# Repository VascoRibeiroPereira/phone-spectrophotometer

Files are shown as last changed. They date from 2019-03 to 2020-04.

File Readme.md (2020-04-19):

# Phone Spectrophotometer

+ [Version française](#spectrophotometre-pour-telephone)

## <U> Overview </U>

This repository includes all elements related with the Phone Spectrophotometer hardware, facilitating its reproduction by anyone.

Many branches of science makes use of spectrophotometers.
The spectrophotometer is an expensive device with the ability to:
<ul>
  <li>Identify an unknown substance</li>
  <li>Quantify a known substance</li>
</ul>

Other common use of spectroscopy with the upmost importance is <b>Teaching</b> the instrumental technique and [Beer'slaw](https://en.wikipedia.org/wiki/Beer%E2%80%93Lambert_law).

The Phone Spectrophotometer is an open source hardware that comits with a reduced cost of production, open source and available for everyone, and uses pre-existing technology - your own mobile phone.

You can also find the .stl files for printing at Thingiverse https://www.thingiverse.com/thing:3185420

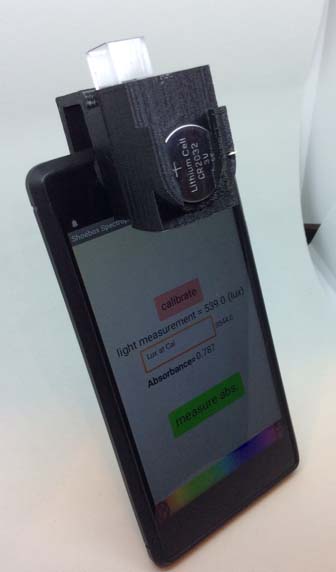
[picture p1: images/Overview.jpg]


This work is licensed under a Solderpad Hardware Licence Version 2.0

## Spectrophotometre pour telephone

### <U>Vue d'ensemble</U>

Ce dépôt comprend tous les éléments liés au matériel du spectrophotomètre pour un ordiphone, facilitant sa reproduction par quiconque.

De nombreuses branches de la science utilisent des spectrophotomètres. Le spectrophotomètre est un appareil coûteux qui permet de :

<ul>
    <li>D'identifier une substance inconnue</li>
    <li>Quantifier une substance connue</li>
</ul>

<b>L'enseignement</b> de la technique des instruments et de la [loi de Beer](https://fr.wikipedia.org/wiki/Loi_de_Beer-Lambert) est un autre usage courant de la spectroscopie qui revêt une importance capitale.

Le spectrophotomètre pour ordiphone est un matériel à code source ouvert, à coût de production réduit, disponible pour toute personne, et qui utilise une technologie préexistante - votre propre téléphone portable.

Vous pouvez également trouver les fichiers .stl à imprimer sur le site Thingiverse <https://www.thingiverse.com/thing:3185420>



Cette réalisation est sous licence Solderpad Hardware Licence Version 2.0

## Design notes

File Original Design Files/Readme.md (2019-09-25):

# Original and Auxiliary Design Files

You will find here the original design files, all made with <i> SketchUp Make</i>, in .skp (its native proprietary format).

To edit it you'll need to download SketchUp Make from [here](https://www.sketchup.com/download/make)

If you only want the auxiliary design files you can use the stereolithography file format (.stl)

___
## Add of the steadyversion!

The Steady Version solves an issue related to the block position not being fixed into the Phone holder. This way it allows more confidence in calibration curves and further results with reproducibility.

_Important note_: I recommend printing the LED Block - Steady Version horizontally.

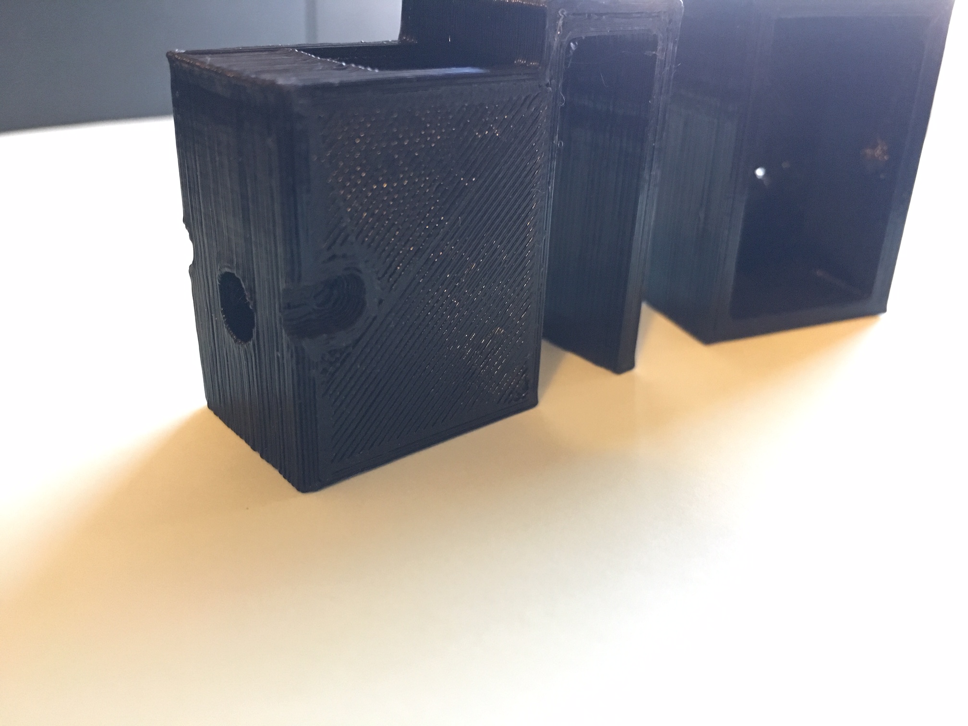
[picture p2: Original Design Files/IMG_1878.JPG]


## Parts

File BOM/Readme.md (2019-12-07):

<h1> Bill of Materials</h1>

|Designator|Description                |Suplier                      |Part Number    |Price |Link                                                                                                                                                                                                           |Notes                                         |
|----------|---------------------------|-----------------------------|---------------|---------|---------------------------------------------------------------------------------------------------------------------------------------------------------------------------------------------------------------|----------------------------------------------|
|A         |LED 400nm                  |SparkFun                     |COM-08662      |0.84 €|https://www.sparkfun.com/products/8662                                                                                                                                                                         |                                              |
|B         |LED 465nm                  |SparkFun                     |COM-00529      |0.30 €|https://www.sparkfun.com/products/9662                                                                                                                                                                         |Quantity discount                             |
|C         |LED 587nm                  |SparkFun                     |COM-00530      |0.30 €|https://www.sparkfun.com/products/10023                                                                                                                                                                        |Quantity discount                             |
|D         |PLA LED Block              |Self Made                    |N/A            |0.22 €|https://fillamentum.com/products/fillamentum-pla-extrafill-traffic-black                                                                                                                                       |Price calculated for the material used (8g)   |
|E         |CR2032 Battery             |SparkFun                     |PRT-00338      |1.71 €|https://www.sparkfun.com/products/338                                                                                                                                                                          |                                              |
|F         |PLA Cuvette Holder         |Self Made                    |N/A            |0.34 €|https://fillamentum.com/products/fillamentum-pla-extrafill-traffic-black                                                                                                                                       |Price calculated for the material used (12g)  |
|G         |Plastic Cuvette            |BrandTech                    |759071D        |0.17 €|https://www.brandtech.com/product/ps-and-pmma-cuvettes/                                                                                                                                                        |Sold in pack of 100. Price for single cuvette.|
|H         |Self-adhesive Holled Rubber|Yelanon                      |ASIN B07NSV2L6B|0.33 €|https://www.amazon.com/Yelanon-Furniture-Pads-Slip-Rubber/dp/B07NSV2L6B/ref=sr_1_30_sspa?crid=220LWP6C13XBT&keywords=furniture+pads&qid=1551634657&s=gateway&sprefix=furniture+%2Caps%2C255&sr=8-30-spons&psc=1|Quantity discount                             |
|I         |Mobile phone               |N/A                          |N/A            |N/A   |N/A                                                                                                                                                                                                            |Pre-existing technology                       |
|J         |Software                   |Shoebox spectrophotometer APP|N/A            |Free  |https://play.google.com/store/apps/details?id=appinventor.ai_billhosker.Shoeboxspec&hl=pt_PT                                                                                                                   |                                              |

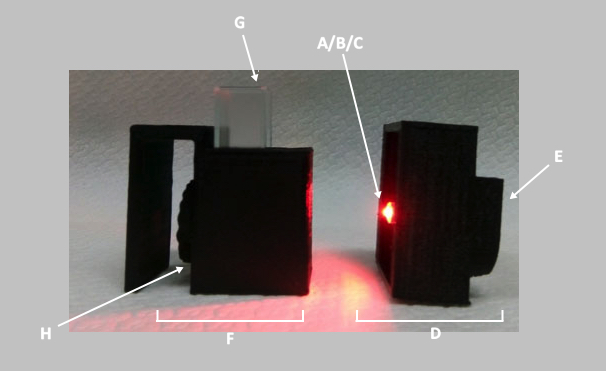
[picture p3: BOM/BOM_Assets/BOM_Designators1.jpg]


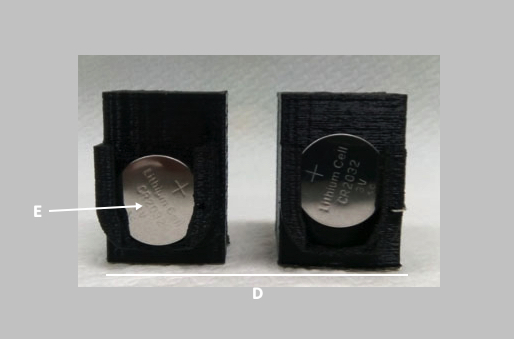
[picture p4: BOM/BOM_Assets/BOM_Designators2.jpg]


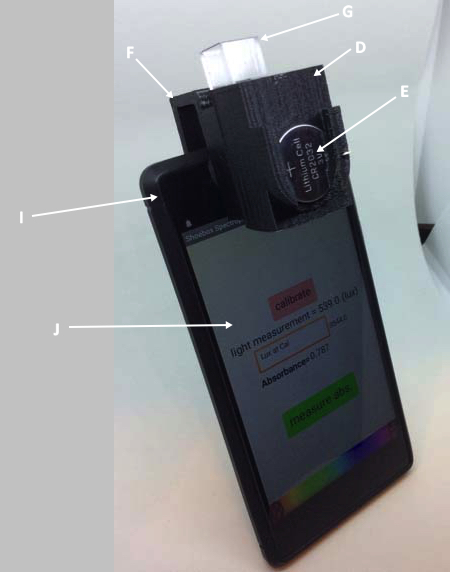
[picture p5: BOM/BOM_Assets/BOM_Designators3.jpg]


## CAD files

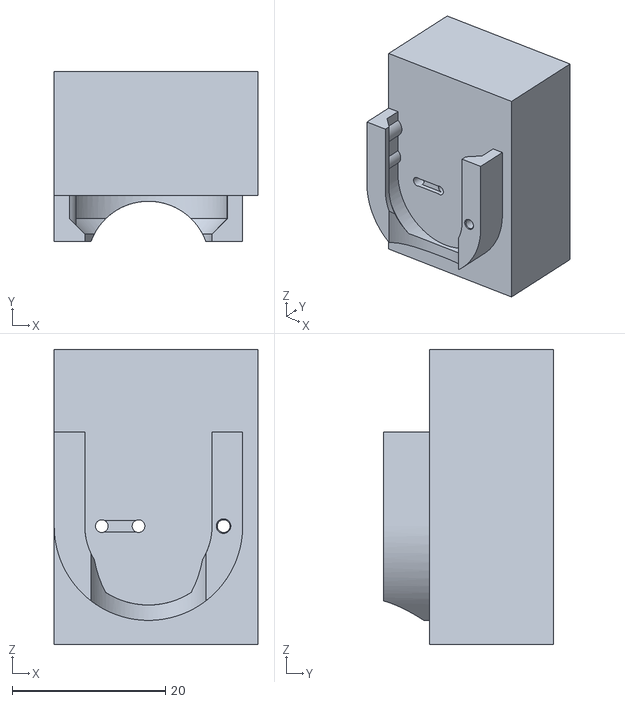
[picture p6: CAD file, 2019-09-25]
Original Design Files/SteadyLEDBlock.stl
26.6 x 22.2 x 38.5

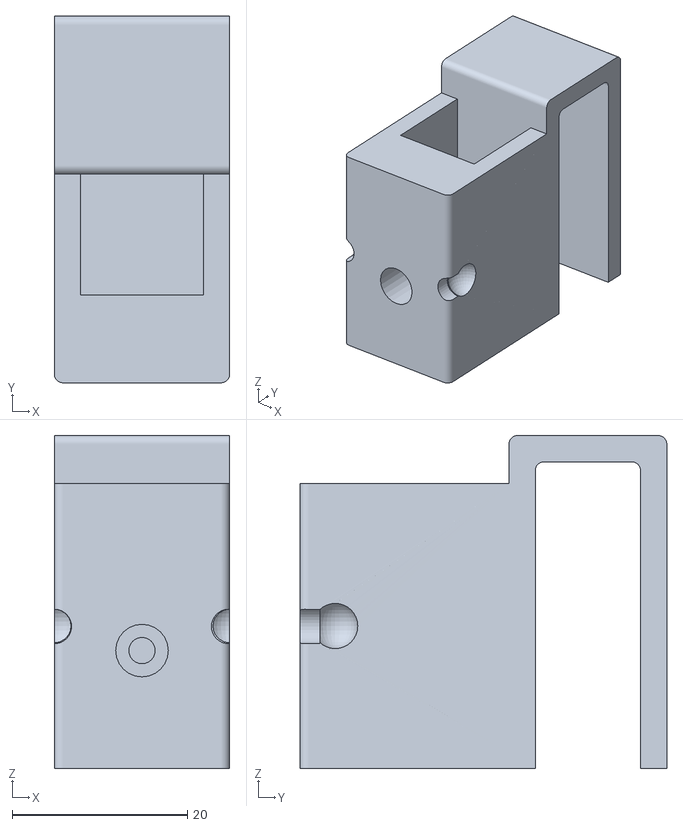
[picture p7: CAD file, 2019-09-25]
Original Design Files/SteadyPhoneHolder.stl.stl
20.0 x 41.8 x 38.0

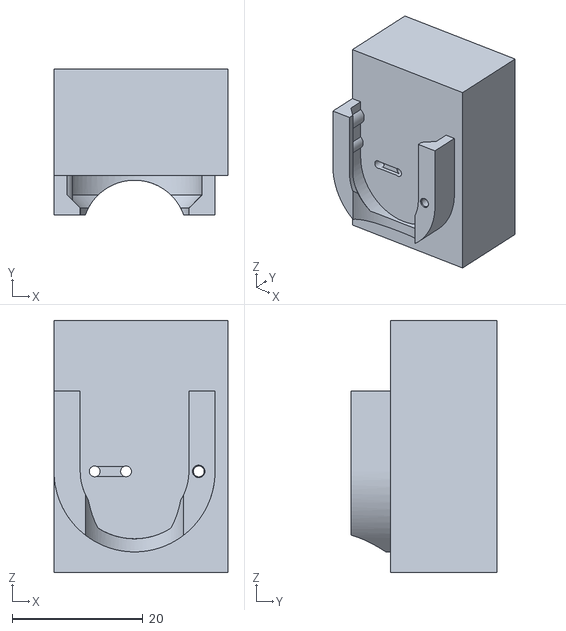
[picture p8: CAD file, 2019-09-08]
Original Design Files/LED_Block.stl
26.6 x 22.2 x 38.5

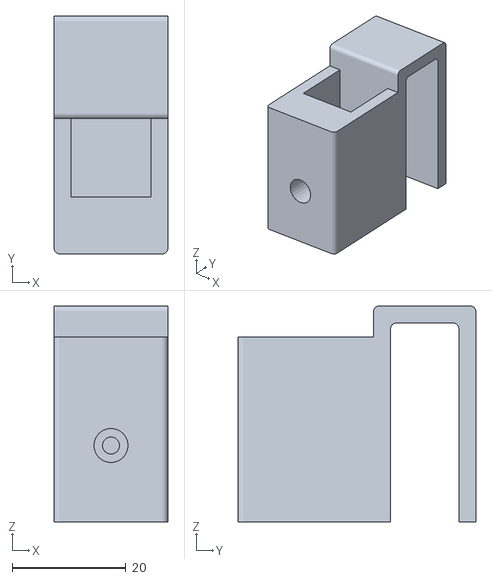
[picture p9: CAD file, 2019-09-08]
Original Design Files/Spectrometer.stl
20.0 x 41.8 x 38.0

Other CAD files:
Original Design Files/Phone Spectrophotometer.skp
Original Design Files/SteadyVersion.skp

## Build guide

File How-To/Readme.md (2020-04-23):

+ [Version française](#comment-travailler-avec-le-spectrophotometre-sur-ordiphone)

## How to Work With the Phone Spectrophotometer

The Phone Spectrophotometer is quite easy to work with. You'll find here documentation showing how to work with it, some advices/troubleshootings and also suggestions of activities.

After the assembly of the <b>LED Block</b> and <b>Cuvette Holder</b> is time to test it out.

To do so, you’ll need an Android Phone with the Shoebox Spectrophotometer APP installed (here on play store https://play.google.com/store/apps/details?id=appinventor.ai_billhosker.Shoeboxspec&hl=en_US and here the source Apk https://androidcrew.com/app/appinventor.ai_billhosker.Shoeboxspec). You can also try other APPs with Ambient Light Sensor measurement.

<i>Note: In iPhone and iPad you can also use alternative APPs but they will measure the light on camera and not on the Light Sensor (usually next to the front camera of your phone).</i>

Turn on the LED by putting the coin battery CR2032 in the on-position (figure 1).



<i>Figure 1. Coin battery in on-position (left) and off-position (right)</i>

Next install the model in the phone with the APP launched and try to get an high value of light measurement (figure 2).

<i>Note: Some phone sensors may be more sensible to light than others, causing them to saturate (give a maximum value). The value obtained from a saturated sensor can not be used because it means the sensor can’t read all the light thats reaching it. Try to misalign the model just enough for the value of the light measurement seams to variate.</i>



<i>Figure 2. Assembled model and phone with the Shoebox Spectrophotometer launched</i>

Now is up to what you want to test! Try the examples in the <b>booklet of spectroscopy activities</b> for you to get used with the technic and the hardware/software.

<ins>Note: If you use other softwares you’ll need to calculate manually the absorbance based on the Raw Data obtained (light measurement).</ins>

You can make the <b>LED Block</b> with many different LED colours. Here are some typical emission wavelengths from coloured LEDs.

<b>Typical LED Wavelengths</b>

Red Light Diodes - 625nm

Green Light Diodes - 525nm

Blue Light Diodes - 465nm

Orange Light Diodes - 610nm

Yellow Light Diodes - 575nm

<em>Special LEDs</em>

IR Light Diodes - 950nm

UV Light Diodes - 400nm

## Comment travailler avec le spectrophotometre sur ordiphone

Le spectrophotomètre avec odiphone est assez facile à utiliser. Vous trouverez ici une documentation montrant comment l'utiliser, quelques conseils et dépannages ainsi que des suggestions d'activités.

Après l'assemblage du <b>bloc LED</b> et du porte-cuvette, il est temps de le tester.

Pour ce faire, vous aurez besoin d'un téléphone Android avec l'application spectrophotomètrie Shoebox installée (ici sour le play store https://play.google.com/store/apps/details?id=appinventor.ai_billhosker.Shoeboxspec&hl=en_US et ici son Apk https://androidcrew.com/app/appinventor.ai_billhosker.Shoeboxspec). Vous pouvez également essayer d'autres APP avec la mesure du capteur de lumière ambiante.

<i>Remarque : sur l'iPhone et l'iPad, vous pouvez également utiliser d'autres APP mais elles mesureront la lumière sur l'appareil photo et non sur le capteur de lumière (généralement à côté de l'appareil photo avant de votre téléphone).</i>

Allumez la LED en mettant la pile CR2032 en position allumée (figure 1).



<i>Figure 1. Batterie de pièces en position marche (à gauche) et en position arrêt (à droite)</i>

Ensuite, installez le modèle dans le téléphone avec l'application lancée et essayez d'obtenir une valeur élevée de mesure de la lumière (figure 2).

<i>Remarque : certains capteurs du téléphone peuvent être plus sensibles à la lumière que d'autres, ce qui les fait saturer (donnez une valeur maximale). La valeur obtenue à partir d'un capteur saturé ne peut pas être utilisée car cela signifie que le capteur ne peut pas lire toute la lumière qui l'atteint. Essayez de désaligner le modèle juste assez pour que la valeur de la mesure de la lumière varie.<i>



<i>Figure 2. Modèle assemblé et téléphone avec le spectrophotomètre Shoebox lancé</i>

Maintenant, c'est à vous de choisir ce que vous voulez tester ! Essayez les exemples du <b>livret d'activités sur la spectroscopie</b> pour vous familiariser avec la technique et le matériel/logiciel.

<ins>Note : Si vous utilisez d'autres logiciels, vous devrez calculer manuellement l'absorbance sur la base des données brutes obtenues (mesure de la lumière).</ins>

Vous pouvez fabriquer le <b>bloc de LED</b> avec de nombreuses couleurs de LED différentes. Voici quelques longueurs d'onde d'émission typiques des LED de couleur.

<b>Longueurs d'onde types des LED</b>

Diodes rouges - 625nm

Diodes lumineuses vertes - 525nm

Diodes lumineuses bleues - 465nm

Diodes lumineuses orange - 610nm

Diodes lumineuses jaunes - 575nm

<em>LEDs spéciaux</em>

Diodes lumineuses IR - 950nm

Diodes de lumière UV - 400nm

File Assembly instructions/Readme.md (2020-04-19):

**Assembly instructions**

+ [Version Française](#instruction-pour-assemblage)

After sourcing the materials described in the BOM start assembling the parts as described in this document.

**3D printed parts**

There are two parts to be 3D printed - the PLA LED block and the Cuvette Holder.

You can use a 3D printer service online or in your local community, or even print it yourself.
If you are going to print it yourself the the recommended settings to 3D print are described in the table 1 (using Ultimaker Cura software).

<i>Table 1 - Main characteristics used to 3D print the Phone Spectrometer</i>

|  Characteristic |  Selection |
|:-:|:-:|
| Layer height  |  0.2mm |
|  Wall thickness |  2mm |
| Top/Bottom thickness  | 0.8mm  |
|  Infill density |  20% |
| Printing temperature  | 210ºC  |
|  Retraction | Enabled  |
| Print speed  | 50mm/s  |
| Generate support  |  No |
|  Build plate adhesion type | Brim  |

Since the 3D printed method is by Fused Deposition Manufacturing the layers are horizontal. This means that the cuvette holder may be fragile at some key parts, and may easily snap. We recommend you to 3D print the cuvette holder horizontally so you have a stronger and much durable part to work with (figure 1).

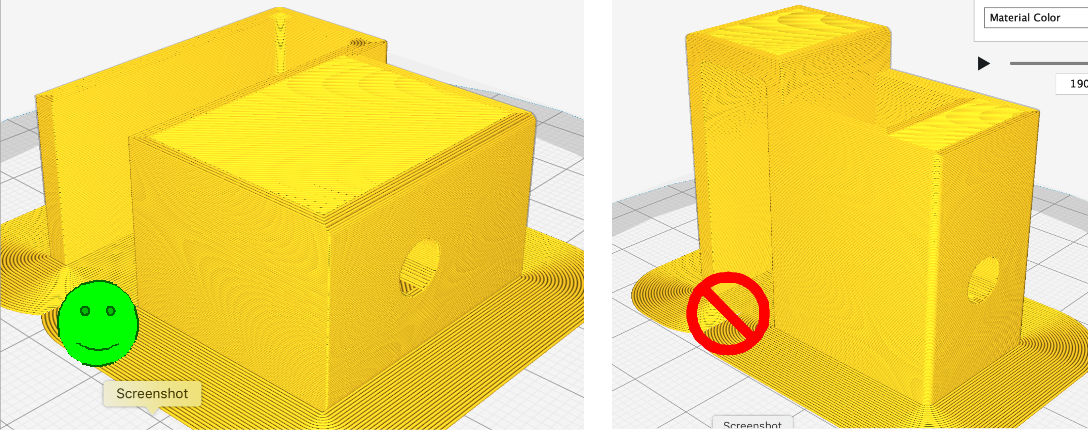
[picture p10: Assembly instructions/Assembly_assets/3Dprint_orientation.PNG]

<i>Figure 1 - Recommended orientation to 3D print the Cuvette Holder</i>

The recommended material to 3D print is a Traffic Black PLA filament (RAL 9017), from Fillamentum Manufacturing Czech s.r.o. or equivalent. 

**Cuvette Holder**

This part only requires the addition of the rubber part (i.e. figure 2)

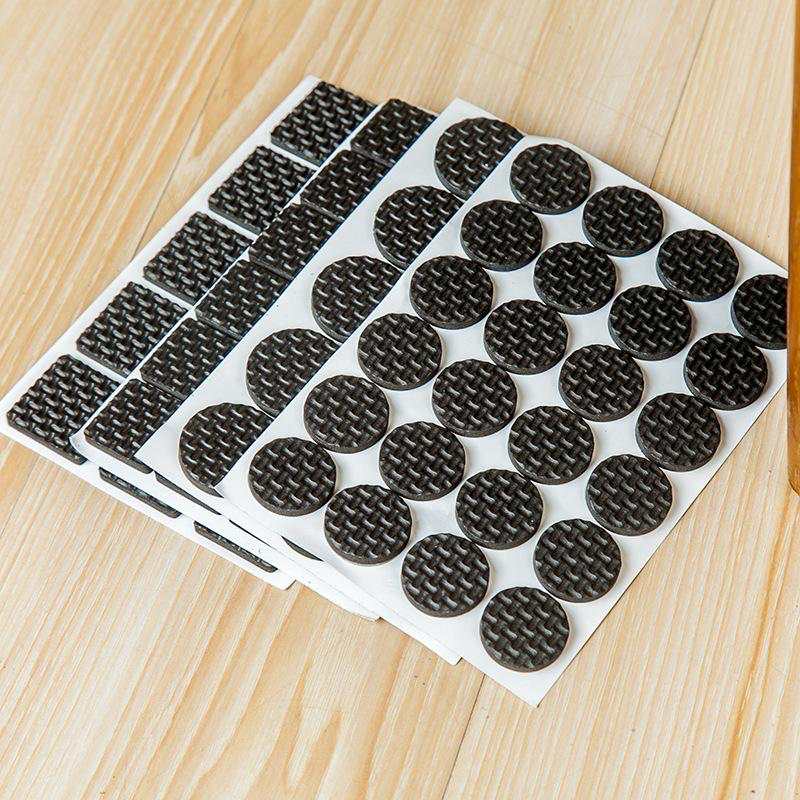
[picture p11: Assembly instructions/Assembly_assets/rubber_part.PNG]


<i>Figure 2 - Rubber part to be glued to the cuvette holder.</i>

Use a puncher to do a hole in the middle of the rubber
Glue it tightly aligned to the rear aperture of the cuvette holder so it will stay between the light exit and the phone sensor - as seen in the BOM designators doc.

This rubber will help you align the rear hole with the phone sensor to get the maximum light measurement possible and also limit the ambient light to interfere with the sensor.

**LED Block**

The LED you choose to use depends on the analyte; for instance, you can have several PLA LED Blocks with different LED mounted and so different emission wavelengths.

To mount the LED you have to identify the LED cathode (-) and anode (+) - figure 3.

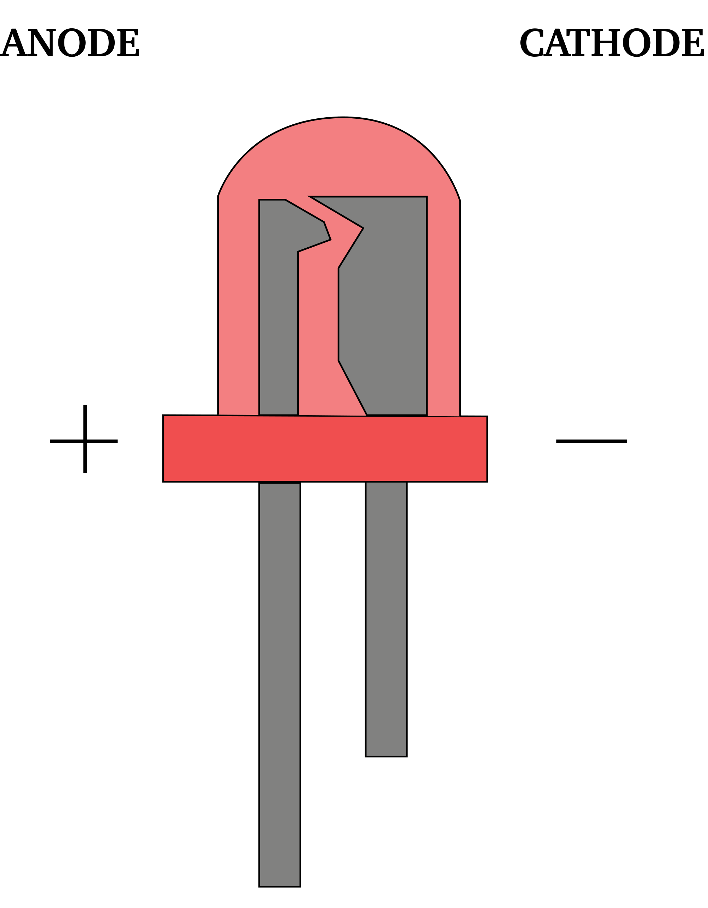
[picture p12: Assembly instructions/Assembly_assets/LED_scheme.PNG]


<i>Figure 3 - A simple scheme of how to identify the cathode and the anode legs of an LED.</i>

Next, mount the LED as specified in figure 4.

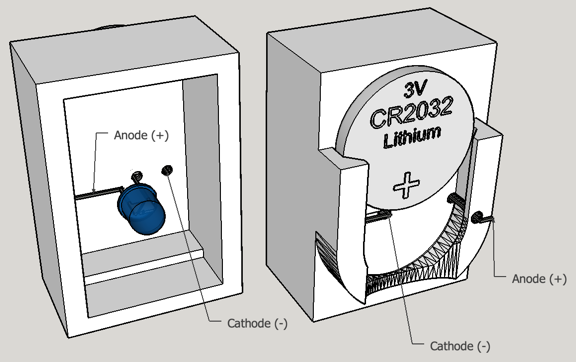
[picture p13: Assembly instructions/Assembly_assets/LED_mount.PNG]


<i>Figure 4 - LED mounted in the printed block, with a CR2032 battery. The anode passes trough the right hole to the outside, touching the battery when it is in the down position and the cathode passes in the first hole to the outside and them to the further left hole to the inside of the model, creating a loop.</i>

The two parts - LED Block and Cuvette Holder fit together and the LED goes inside the front aperture of the Cuvette Holder - it may be necessary to adjust the LED position the first time.

**Finish**

After the assembly of the parts, turn on the LED and mount it with the rear hole pointed near the front camera of your phone. Open the Shoebox Spectrophotometer APP (here on play store https://play.google.com/store/apps/details?id=appinventor.ai_billhosker.Shoeboxspec&hl=en_US and here the source Apk https://androidcrew.com/app/appinventor.ai_billhosker.Shoeboxspec), start moving the model checking the light measure to figure when the light gets to the sensor - you should get reading from 0, when the rear hole is completely misaligned, to a big value like 4000 for example (this depends on the sensor of your phone).

<ins>Note:</ins>

If the LED Block have a loose fit to the Cuvette Holder you may use something so it remains stable (such as a little piece of paper between the models, or an elastic rubber). You may even glue it if you don’t intend to change the LED Block.
The LED Block turns on when the coin battery in down and off when the battery is up.
You can use the LED Block turned on to help you glue the rubber part to the Cuvette Holder.
Do not use the APP when the light measurement seams to be at the highest value possible. Move a little the holder so it slightly misalign with the sensor and gets a more variable value so the sensor is not saturated with light.

## Instruction pour assemblage

Après avoir sélectionné les matériaux décrits dans la nomenclature, commencez à assembler les pièces comme décrit dans ce document.

**Pièces imprimées en 3D**

Il y a deux parties à imprimer en 3D : le bloc LED PLA et le porte-cuvette.

Vous pouvez utiliser un service d'impression 3D en ligne ou dans votre communauté locale, ou même l'imprimer vous-même. Si vous comptez l'imprimer vous-même, les paramètres recommandés pour l'impression 3D sont décrits dans le tableau 1 (à l'aide du logiciel Ultimaker Cura).

<i>Tableau 1 - Principales caractéristiques utilisées pour l'impression 3D du spectromètre téléphonique</i>

| Caractéristiques | Selection |
|:-:|:-:|
| Hauteur de la couche | 0,2 mm |
| Epaisseur de la paroi | 2mm |
| Épaisseur du dessus/du dessous | 0,8 mm |
| Densité de remplissage | 20 |
| Température d'impression | 210ºC |
| Rétraction | activée |
| Vitesse d'impression | 50mm/s |
| Générer un support | Non |
| Construire une plaque d'adhérence typée | Brim |

Comme la méthode d'impression en 3D est celle de la fabrication par dépôt fondu, les couches sont horizontales. Cela signifie que le porte-cuvette peut être fragile à certains endroits clés et peut facilement se casser. Nous vous recommandons d'imprimer en 3D le porte-cuvette à l'horizontale afin d'avoir une pièce plus solide et plus durable pour travailler (figure 1).



<i>Figure 1 - Orientation recommandée pour l'impression 3D du porte-cuvette</i>

Le matériau recommandé pour l'impression 3D est un filament PLA Traffic Black (RAL 9017), de Fillamentum Manufacturing Czech s.r.o. ou équivalent.

**Porte-cuvette**

Cette partie ne nécessite que l'ajout de la partie en caoutchouc (c'est-à-dire la figure 2)



<i>Figure 2 - Pièce en caoutchouc à coller sur le porte-cuvette.</i>

Utilisez un poinçon pour faire un trou au milieu du caout. Cochouc. Collez la pièce fermement alignée sur l'ouverture arrière du porte-cuvette afin qu'elle reste entre la sortie de la lumière et le capteur du téléphone − comme indiqué dans le document des désignations de la nomenclature.

Ce caoutchouc vous aidera à aligner le trou arrière avec le capteur du téléphone pour obtenir la mesure de lumière maximale possible et aussi limiter la lumière ambiante pour interférer avec le capteur.

**Bloc de LED**

La LED que vous choisissez d'utiliser dépend de l'analyte ; par exemple, vous pouvez avoir plusieurs blocs de LED PLA avec différentes LED montées et donc différentes longueurs d'onde d'émission.

Pour monter la LED, vous devez identifier la cathode (-) et l'anode (+) de la LED - figure 3.



<i>Figure 3 - Un schéma simple pour identifier la cathode et les pattes d'anode d'une LED.</i>

Ensuite, montez la LED comme indiqué sur la figure 4.


<i>Figure 4 - LED montée dans le bloc imprimé, avec une pile CR2032. L'anode passe à travers le trou de droite vers l'extérieur, touchant la pile lorsqu'elle est en position basse et la cathode passe dans le premier trou vers l'extérieur et eux dans le trou plus à gauche vers l'intérieur du modèle, créant ainsi une boucle.</i>

Les deux parties - le bloc de LED et le porte-cuvette s'emboîtent et la LED passe dans l'ouverture avant du porte-cuvette - il peut être nécessaire d'ajuster la position de la LED la première fois.

**Terminer**

Après l'assemblage des pièces, allumez la LED et placez la avec sur trou arrière pointé près de la caméra avant de votre téléphone. Ouvrez l 'application de spectrophotomètrie de Shoebox (ici sour le play store https://play.google.com/store/apps/details?id=appinventor.ai_billhosker.Shoeboxspec&hl=en_US et ici son Apk https://androidcrew.com/app/appinventor.ai_billhosker.Shoeboxspec), commencez à déplacer le modèle en vérifiant la mesure de la lumière pour savoir quand la lumière arrive au capteur − vous devriez obtenir une lecture de 0, lorsque le trou arrière est complètement désaligné, à une grande valeur comme 4000 par exemple (cela dépend du capteur de votre téléphone).

<ins>Note :</ins>

Si le bloc de LED est mal ajusté au porte-cuvette, vous pouvez utiliser quelque chose pour qu'il reste stable (comme un petit morceau de papier entre les pièces assemblées, ou un élastique). Vous pouvez même le coller si vous n'avez pas l'intention de changer le bloc de LED. Le bloc LED s'allume lorsque la pile est déchargée et s'éteint lorsque la pile est pleine. Vous pouvez utiliser le Bloc LED allumé pour vous aider à coller la partie en caoutchouc sur le Porte-cuvette. N'utilisez pas l'application lorsque la mesure de la lumière semble être à la valeur la plus élevée possible. Déplacez un peu le support pour qu'il s'aligne légèrement sur le capteur et obtienne une valeur plus variable afin que le capteur ne soit pas saturé de lumière.

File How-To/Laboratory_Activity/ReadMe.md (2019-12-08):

# Laboratory Activity

<ins>Objectives</ins>

**- Lambert-Beer Law verification**

**- Sample Assay**

## Lambert-Beer Law verification

For the experimental activity we will need access to a spectrophotometer and to one or more sets of coloured filters. One can use professional materials or, in this case:

- An Android phone with an ALS (ambient light sensor) and the APP “Shoebox Spectrophotometer"

- Spectrophotometer and light source (fixed wavelength from a LED) made by 3D printing or other creative method.

- Coloured filters with 9mm x 30mm.

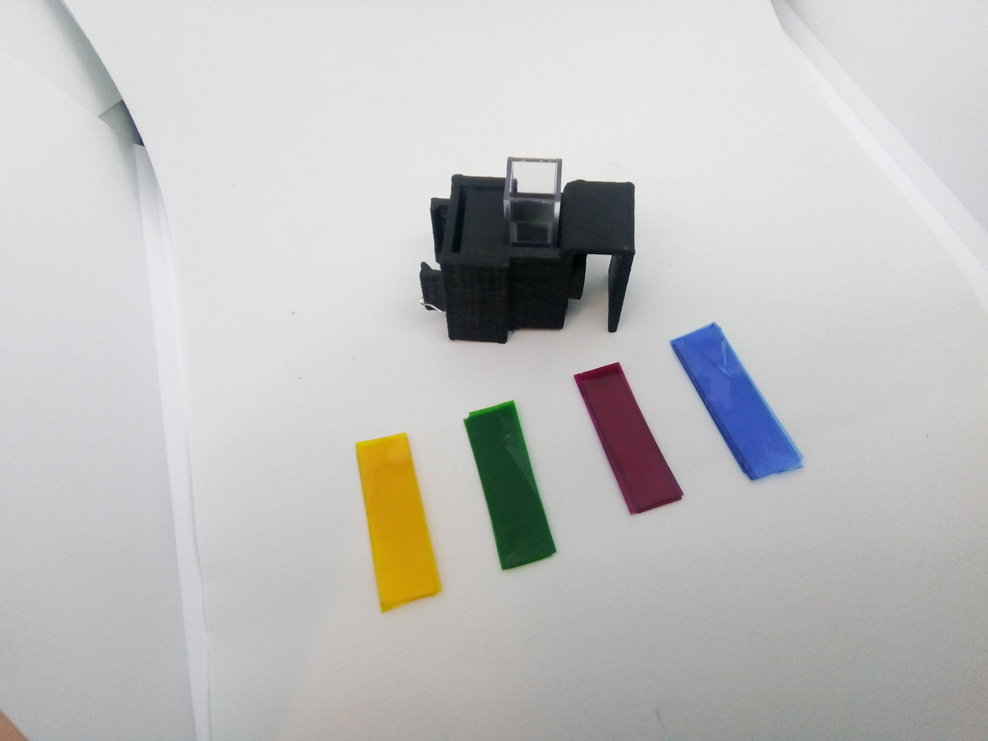
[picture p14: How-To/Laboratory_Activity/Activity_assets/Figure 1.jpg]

*Figure 1 - Fixed wavelength spectrophotometer and filters used*

When using LEDs we assume the wavelengths in the table 1.

*Table 1 - Maximum emitted wavelength of coloured LED*

|LED   |Emitted Wavelengh (max)|
|------|-----------------------|
|Red   |625nm                  |
|Green |525nm                  |
|Blue  |465nm                  |
|Orange|610nm                  |
|Yellow|575nm                  |

### Procedure

1. Mount the spectrophotometer with the LED turned on and with the APP launched.

2. Adjust the equipment until you obtain a LUX reading that is high.

3. Register the approximate value of the LUX measured and take note of this value as you add filters to the spectrometer.

### Data Processing

Assuming that the first value of LUX corresponds to 100% of transmittance, start to calculate the percentage of transmittance of each filter assuming the  previous LUX measure.

#### Questions to be answered:

> All the filters give us the same percentage?
> 
> What can we say about the linearity needed for the Lambert-Beer Law?
_____

**Lets start with this example:**

We used a LED of 525nm (green) and started adding yellow filters. The LUX data are in the table 2.

*Table 2 - Data obtained at 525nm for yellow filters*

|Number of Filters|Lux  |
|-----------------|-----|
|0                |13150|
|1                |9830 |
|2                |7580 |
|3                |5640 |
|4                |4540 |
|5                |3630 |
|6                |2850 |

Next we processed the data in order to understand if we maintain the linearity - if one filter gives us an aberrant reading - out of the expected percentage.

We can check in table 3, that for each new filter added our source loses about 20-25% of intensity. We can say that we must have linearity since the values are in the same order of magnitude.

*Table 3 - % of transmitance for each added filter*

|Number of Filters|% Transmitance|
|-----------------|--------------|
|0                |100           |
|1                |75            |
|2                |77            |
|3                |74            |
|4                |80            |
|5                |80            |
|6                |79            |

After the analysis we can observe the transmittance as we add each filter. The table 4 presents the data expressed in the graphs 1 and 2.

*Table 4 - % of transmitance and absorbance with increased number of added filter*

|Number of Filters|% Transmittance|Absorbance|
|-----------------|---------------|----------|
|0                |100            |0         |
|1                |75             |0,13      |
|2                |58             |0,24      |
|3                |43             |0,37      |
|4                |35             |0,46      |
|5                |28             |0,56      |
|6                |22             |0,66      |

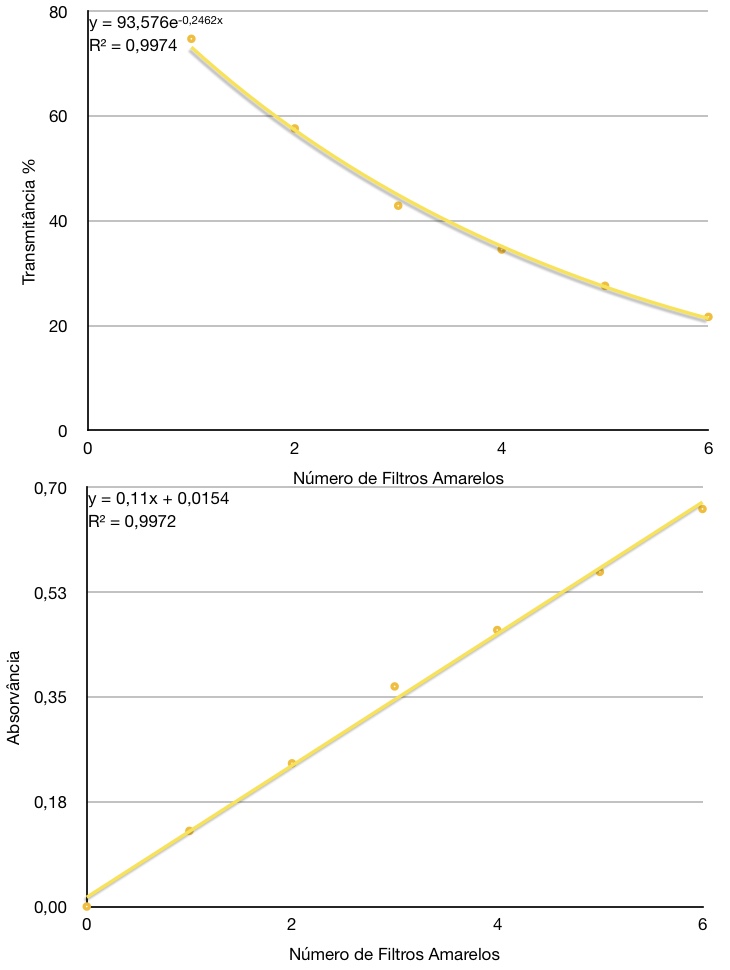
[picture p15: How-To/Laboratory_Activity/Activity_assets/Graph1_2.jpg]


*Graph 1 and 2 - Transmitance and absorbance versus number of filters*

We have here an experimental evidence that the transmittance decreases in a logarithmic fashion and the absorbance remains linear. We will check next what happens in a linearity loss case.

_____

With the same light source we tested pink coloured filters.

The data obtained and its processing are condensed in the table 5. We can observe that the percentage of the retained radiation for each filter is very inconsistent.

*Table 5 - Data obtained and processed of the pink filters at 525nm*

|Number of Filters|LUX  |%Transmitance/Filter|%Transmitance|Absorbance|
|-----------------|-----|--------------------|-------------|----------|
|0                |12500|100                 |100          |0         |
|1                |368  |2,9                 |2,9          |1,5       |
|2                |33   |9                   |0,3          |2,6       |
|3                |14   |42,4                |0,1          |3         |
|4                |10   |71,4                |0,1          |3,1       |
|5                |6    |60                  |0            |3,3       |
|6                |6    |100                 |0            |3,3       |

By this analysis we notice that the absorbance is not linear with the number of filters added but more like logarithmic.

One indicator of a good linear regression is a R<sup>2</sup> close to, or higher than 0,9, which is not the case here.

Note that in visible spectroscopy the usual values of absorbance are less than 1 AU, to minimize the effects of light dispersion and loss of linearity.

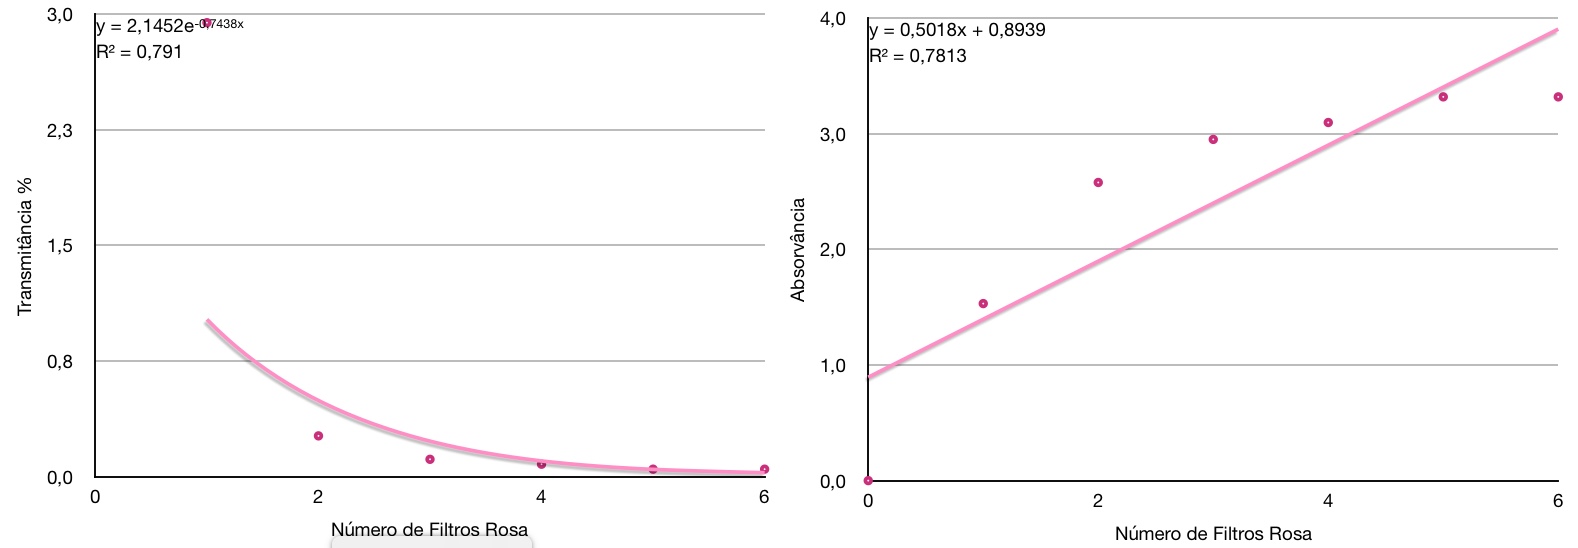
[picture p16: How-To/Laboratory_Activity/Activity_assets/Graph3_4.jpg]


*Graph 3 and 4 - Transmitance and absorbance of pink filters at 525nm*

_____

## Sample Assay

### Indigo Carmine in blue Pills

<ins>Notice:</ins> This procedure is only a demonstration and can be used for any coloured sample, using the right wavelength.

> How do we choose the wavelength with which we will analyse a sample?

	We want to minimize the error and use a typical maximum of the spectrum of the analyte.
	For that we need the molecule spectrum from bibliography or experimentally obtained.
	We used the literature available online to check the best wavelength to analyse the blue pills.
	To analyse the Indigo Carmine present in the blue pills we choosed the 625nm LED (red), that is close enough to the molecule maximum of 610nm.

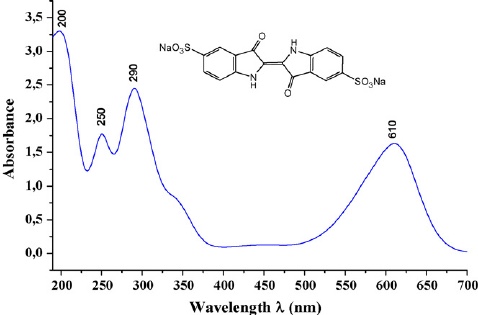
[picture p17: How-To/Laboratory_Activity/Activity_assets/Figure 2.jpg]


*Figure 2 - Absorbance spectra of Indigo Carmine; Bentouami, Abdelhadi & Said Ouali, Mohand & de menorval, Louis-Charles. (2015). 1-s2.0-S1010603010000894-main.*

> To proceed with the assay, is it only needed to obtain the pills absorbance?

	No. We will also need to compare the obtained absorbance with a reference standard.

_____

### Remembering the Lambert-Beer Law
A = 𝓔bc
If we know the value of 𝓔 at the wavelength we are using, theoretically we only need the absorbance. But in our case we don’t know for sure that value, and to minimize the errors in our analysis we need to perform a calibration curve with a standard of known concentration.

**To this work we need:**
- Test tubes
- 5 Volumetric flasks of 20,0 ml and one of 100,0 ml
- Micropipette and volumetric pipetts
- Scale
- Cuvettes
- Deionised water
- Indigo Carmine Standard
- Filters of porosity <0,45 µm

### Procedure
1. Weight 100 mg of standard to the 100,0 ml volumetric flask and dilute with water.
2. Disintegrate 10 pills in 10,0 ml of water, and filter.
3. Measure 250 µl, 500 µl, 1 ml, 2 ml and 3 ml of the standard to each volumetric flask of 20,0 ml and add water.
4. Measure the absorbances of the standards and the sample with the APP Shoebox Sectrophotometer using water as blank.
5. Make a calibration curve with the standards and determine the concentration of blue colorant per pill.

### Results
From developing the linear regression equation obtained to the sample absorbance we conclude that each pill have 0,45 mg of indigo carmine colorant (see table 6 and graph 5).
This work can also be applied to drinks, candies, and everything that have colour.

*Table 6 - Absorbances measured for 102,0mg of standard and sample*

|Concentration mg/mL|Absorbance|
|-------------------|----------|
|0                  |0         |
|0,1275             |0,08      |
|0,255              |0,139     |
|0,51               |0,268     |
|1,02               |0,444     |
|1,53               |0,637     |
|Sample             |0,211     |

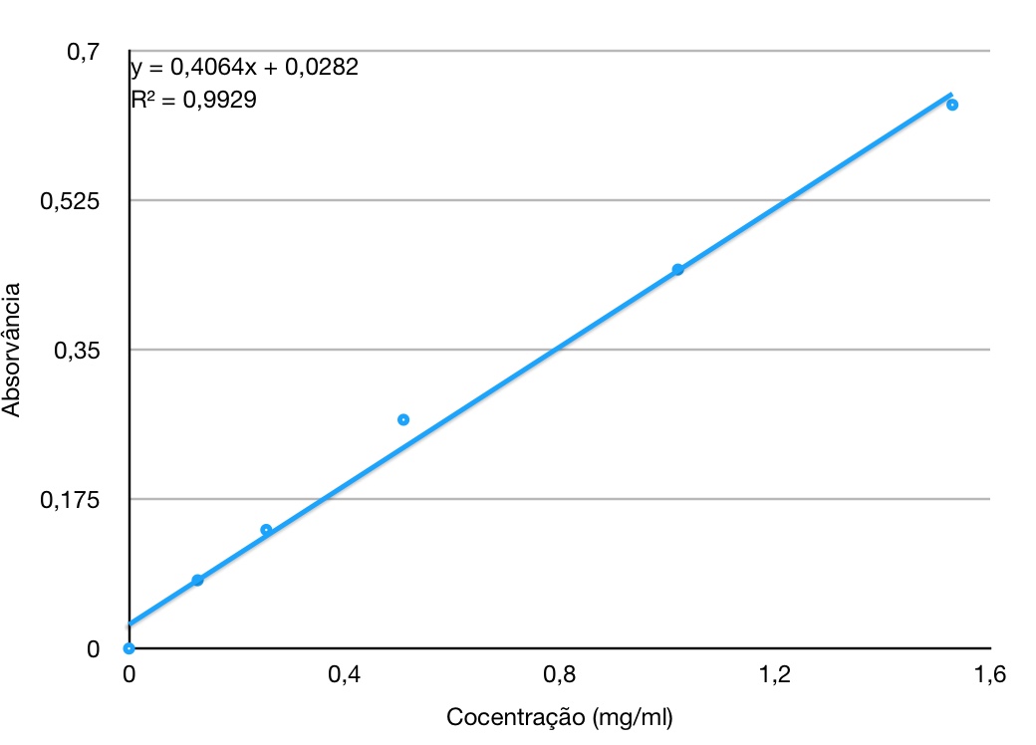
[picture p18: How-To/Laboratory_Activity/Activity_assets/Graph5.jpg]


*Graph 5 - Calibration Curve*

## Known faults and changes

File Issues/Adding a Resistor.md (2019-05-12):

# Enhancement Issue - Adding a Resistor

Issue Link: https://github.com/VascoRibeiroPereira/phone-spectrophotometer/issues/6

Note: this file explains how to add a resistor to the original design. If you want to avoid this procedure you can buy an LED with incorporated resistor like this: https://www.sparkfun.com/products/14560

This issue was considered an enhancement that is not crucial for the use of the phone spectrophotometer but highly beneficial.

The benefits to it's use are mainly:
<ul>
  <li>Prevent the LED from shorts</li>
  <li>Stabilize the current</li>
</ul>

The % of light loss at the beginning of turning on the equipment is ameliorated by adding a resistor.
To apply this enhancement we need to calculate the resistor value, for that we need the Ohm's Law:

<b>R = V / I</b>

Gather this information from your LED:
<ul>
  <li>Forward Voltage drop (Vf) in V </li>
  <li>Max Current (I) in A</li>
</ul>

For example, the Super Bright Red LED from Sparkfun: https://www.sparkfun.com/products/528

Vf = 2,4V <p>
I = 0,02A

If we supply 3V (Vs) from our CR2032 battery, then:

V = Vs - Vf = 3 - 2,4 = 0,6 V

Applying Ohm's Law:

R = 0,06 / 0,02 = 30 Ω

It is needed a resistor as close to 30 Ω as possible. This process must be done to every LED from different wavelengths and manufacturers (because they may differ in characteristics).

<b>How to mount?</b> Simply soldering it to the anode of the LED and use the other end of the resistor as the anode that touches the battery.

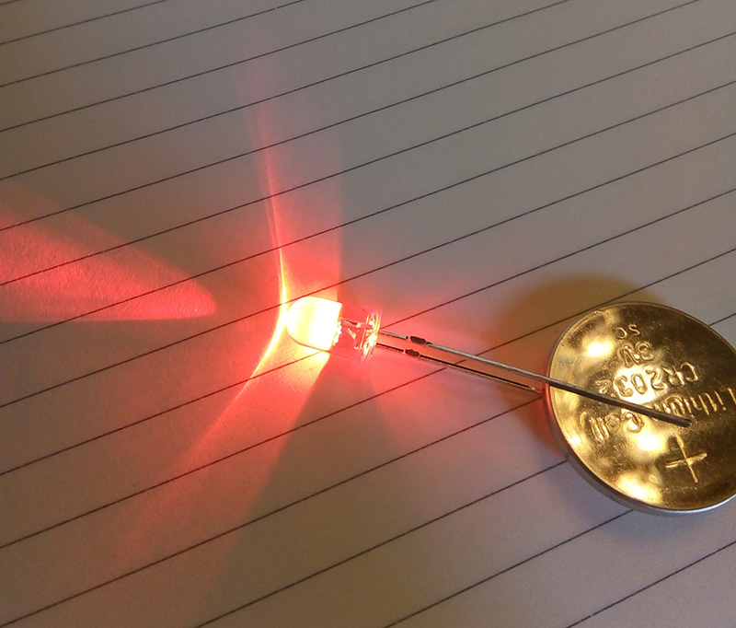
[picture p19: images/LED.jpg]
<p>
LED without resistor

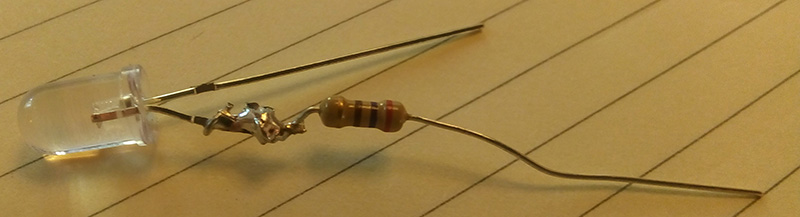
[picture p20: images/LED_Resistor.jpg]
<p>
LED with resistor

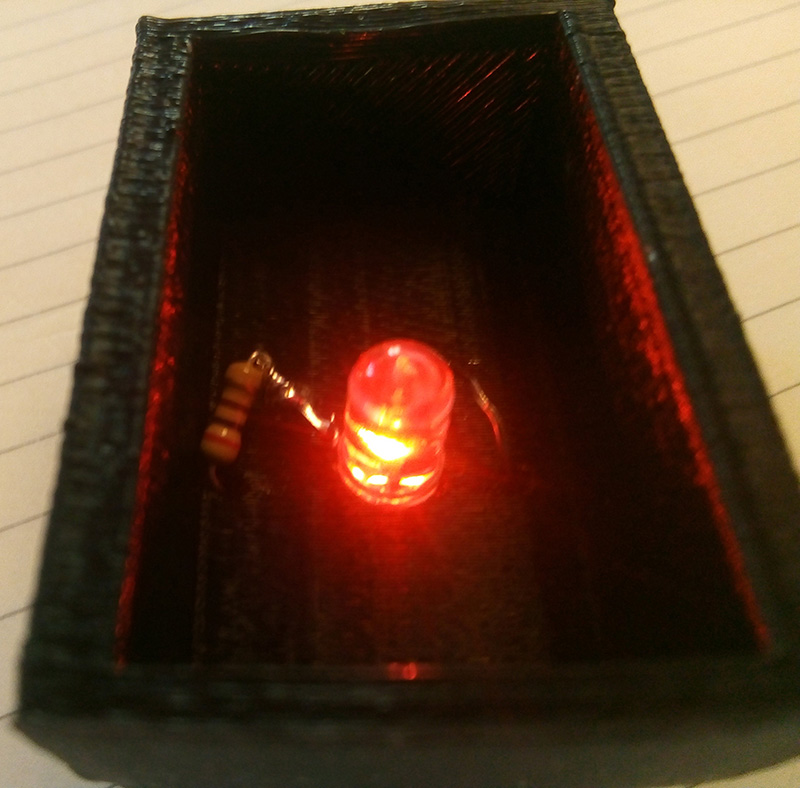
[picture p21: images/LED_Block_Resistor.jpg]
<p>
LED with resistor mounted in the LED Block

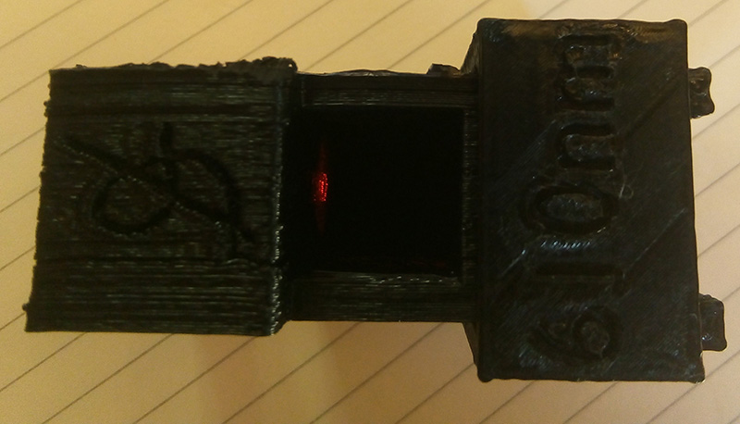
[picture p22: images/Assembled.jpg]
<p>
The LED block + Cuvette block mounted in the resistor version without issues.

3D Planed...

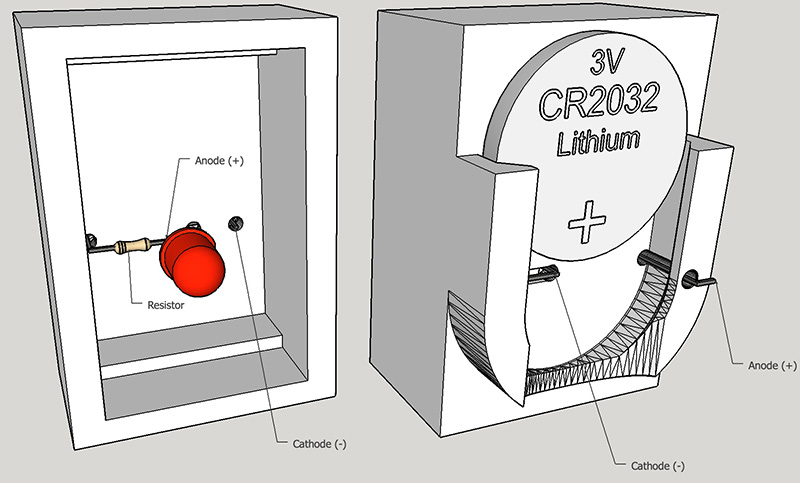
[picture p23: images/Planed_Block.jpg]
<p>

<b>Personal notes from the author:<p>
I never experience a short from using the described materials - CR2032 battery - with any LED. If anyone experience it, please open an issue and I will include the resistors as part of the design!</b>

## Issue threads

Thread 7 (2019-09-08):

### ISSUE TITLE
Oversized STL file in Cura, can't scale down enough to print

### ISSUE THREAD

**Issue by arthurlutz** [VascoRibeiroPereira/phone-spectrophotometer#7]
Opening the STL files in Cura I get *huge* models, trying to put to 1% scale is still not enough to get them to a acceptable size to print. 

![Screenshot from 2019-09-07 09-41-41](https://user-images.githubusercontent.com/108437/64471618-1158c880-d154-11e9-806d-cc483b1a04a4.png)
![Screenshot from 2019-09-07 09-40-55](https://user-images.githubusercontent.com/108437/64471619-1158c880-d154-11e9-9718-20ce041e6c44.png)

Do you know what the problem could be ?

**Comment by VascoRibeiroPereira** [comment]
Hello,
Thank you for your feedback. It's probably because I made some mistake when exporting to stl. I've corrected the models and I've tested successfully in Cura. ;)

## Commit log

2019-05-11 Create Adding a Resistor.md
2019-05-11 Update Adding a Resistor.md
2019-09-08 Corrected model scales
    Answering issue - "Oversized STL file in Cura, can't scale down enough to print #7"
    [LED_Block.stl, Phone Spectrophotometer.skp, Spectrometer.stl]
2019-09-25 Add a "Steady Version"
    [SteadyLEDBlock.stl, SteadyPhoneHolder.stl.stl, SteadyVersion.skp]
2019-12-06 Add images for .md files
    To the assembly instructions .md file
